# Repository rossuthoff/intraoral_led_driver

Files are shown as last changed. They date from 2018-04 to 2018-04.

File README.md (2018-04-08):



# intraoral led driver
Switching boost LED driver based on the Linear Technology [LT3478-1](http://www.analog.com/en/products/power-management/led-driver-ic/buck-boost-led-drivers/lt3478.html) chip. This LED driver is used for the oral cancer screening device described in [1]. 

## related repositories
This design requires the footprints found in the [kicad_footprints](https://github.com/rossuthoff/kicad_footprints) repository. Make sure the library and .mod files are added to your folder search locations. This board utilizes the [ytai/IOIO](https://github.com/ytai/ioio) microcontroller (MCU). Other microcontrollers that can send 3.3 V signals and control an I2C interface may be used. 

## general use
### power supply
LED driver is used in boost mode. The battery voltage must be less than the voltage drop across each individual LED string. Connector J5 supplies power to the MCU.

### led strings
Connect the LED strings to A+/A- and B+/B- connections. The LED string to be illuminated is controlled through a 3.3V signal to the sA or sB pins. The applied current is controlled through a Analog Devices [AD5247](http://www.analog.com/en/products/digital-to-analog-converters/digital-potentiometers/ad5247.html) digital potentiometer with an I2C interface.

# references
[1] Uthoff, R. D. et al. Development of a dual-modality, dual-view smartphone-based imaging system for oral cancer detection. in Proc. SPIE 10486, Design and Quality for Biomedical Technologies XI 10486, 104860V-10486–7 (SPIE, 2018).

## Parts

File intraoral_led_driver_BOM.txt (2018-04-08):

Reference	Locations	Value	Footprint	Notes	Manufacturer	PN	Distributor	Dist PN	Dist Link
C1	1	3.3uF	Capacitors_SMD:C_0603	25V	TDK Corporation	C1608X5R1E335K080AC	Digikey	445-14141-1-ND	https://www.digikey.com/product-detail/en/tdk-corporation/C1608X5R1E335K080AC/445-14141-1-ND/3955807
C2	1	4.7uF	Capacitors_SMD:C_1206	25V	TDK Corporation	C3216X5R1E475K160AA	Digikey	445-4047-2-ND	http://www.digikey.com/product-detail/en/tdk-corporation/C3216X5R1E475K160AA/445-4047-2-ND/1965635
C3	1	10uF	Capacitors_SMD:C_1812	25V	TDK Corporation	C4532X5R1E106M250KA	Digikey	445-3926-2-ND	http://www.digikey.com/product-detail/en/tdk-corporation/C4532X5R1E106M250KA/445-3926-2-ND/1923415
"C4, C6"	2	1uF	Capacitors_SMD:C_0603	25V	TDK Corporation	CGB3B1X5R1E105K055AC	Digikey	445-13224-2-ND	http://www.digikey.com/product-detail/en/tdk-corporation/CGB3B1X5R1E105K055AC/445-13224-2-ND/3950460
"C5, C7"	2	0.1uF	Capacitors_SMD:C_0603		TDK Corporation	C1608X8R1E104K080AA	Digikey	445-2500-2-ND	http://www.digikey.com/product-detail/en/tdk-corporation/C1608X8R1E104K080AA/445-2500-2-ND/927126
C8	1	10uF	Capacitors_Tantalum_SMD:CP_Tantalum_Case-A_EIA-3216-18_Reflow	10V	AVX Corporation	TPSA106K010R1800	Digikey	478-3317-1-ND	https://www.digikey.com/product-detail/en/avx-corporation/TPSA106K010R1800/478-3317-1-ND/930109
D1	1	D_Schottky_AAK	footprints:D_PowerDI-5		Diode Incorporated	PDS560-13	Digikey	PDS560DICT-ND	http://www.digikey.com/product-detail/en/diodes-incorporated/PDS560-13/PDS560DICT-ND/776779
D2	1	LED	footprints:LED_0603		Panasonic Electric Components	LNJ937W8CRA	Digikey	LNJ937W8CRATR-ND	http://www.digikey.com/product-detail/en/panasonic-electronic-components/LNJ937W8CRA/LNJ937W8CRACT-ND/2349027
"J1, J3"	2	CONN_01X04	Connectors_JST:JST_PH_S4B-PH-SM4-TB_04x2.00mm_Angled		JST Sales America	S4B-PH-SM4-TB(LF)(SN)	Digikey	455-1751-1-ND	https://www.digikey.com/product-detail/en/jst-sales-america-inc/S4B-PH-SM4-TB(LF)(SN)/455-1751-1-ND/926848
J2	1	CONN_01X03	Connectors_JST:JST_PH_S3B-PH-SM4-TB_03x2.00mm_Angled		JST Sales America	S3B-PH-SM4-TB(LF)(SN)	Digikey	455-1750-2-ND	https://www.digikey.com/product-detail/en/jst-sales-america-inc/S3B-PH-SM4-TB(LF)(SN)/455-1750-2-ND/926656
"J4, J5"	2	CONN_01X02	Connectors_JST:JST_PH_S2B-PH-SM4-TB_02x2.00mm_Angled		JST Sales America	S2B-PH-SM4-TB(LF)(SN)	Digikey	455-1749-2-ND	http://www.digikey.com/product-detail/en/jst-sales-america-inc/S2B-PH-SM4-TB(LF)(SN)/455-1749-2-ND/926655
L1	1	6.8uH	footprints:Sumida_L_CDRH105R		Sumida America Components	CDRH105RNP-6R8NC	Digikey	308-1927-2-ND	https://www.digikey.com/product-detail/en/sumida-america-components-inc/CDRH105RNP-6R8NC/308-1927-2-ND/3947171
"Q1, Q2"	2	Si2318DS-T1	TO_SOT_Packages_SMD:SOT-23		Vishay Siliconix	SI2318DS-T1-E3	Digikey	SI2318DS-T1-E3TR-ND	http://www.digikey.com/product-detail/en/vishay-siliconix/SI2318DS-T1-E3/SI2318DS-T1-E3DKR-ND/1764691
R1	1	100k	Resistors_SMD:R_0402	1%	Yageo	RC0402FR-07100KL	Digikey	311-100KLRTR-ND	http://www.digikey.com/product-detail/en/yageo/RC0402FR-07100KL/311-100KLRTR-ND/726526
R2	1	24k	Resistors_SMD:R_0402	1%	Yageo	RC0402FR-0724KL	Digikey	311-24KLRTR-ND	http://www.digikey.com/product-detail/en/yageo/RC0402FR-0724KL/311-24KLRTR-ND/2827581
R3	1	69.8k	Resistors_SMD:R_0402	1%	Yageo	RC0402FR-0769K8L	Digikey	YAG3216TR-ND	http://www.digikey.com/product-detail/en/yageo/RC0402FR-0769K8L/YAG3216TR-ND/5281076
"R4, R5, R7, R8"	4	10k	Resistors_SMD:R_0603	1%	Yageo	RC0603FR-0710KL	Digikey	311-10.0KHRTR-ND	https://www.digikey.com/product-detail/en/yageo/RC0603FR-0710KL/311-10.0KHRTR-ND/726880
R6	1	1k	Resistors_SMD:R_0603	1%	Yageo	RC0603FR-071KL	Digikey	311-1.00KHRTR-ND	https://www.digikey.com/product-detail/en/yageo/RC0603FR-071KL/311-1.00KHRTR-ND/726843
SW1	1	SW_SPST	footprints:C&K_SPST_switch_L101011MS02Q		C&K	L101011MS02Q	Digikey	CKC5106-ND	http://www.digikey.com/product-detail/en/c-k/L101011MS02Q/CKC5106-ND/484142
U1	1	LT3478-1	footprints:TSSOP-16-1EP_4.4x5mm_Pitch0.65mm		Linear Technologies	LT3478EFE-1#PBF	Digikey	LT3478EFE-1#PBF-ND	http://www.digikey.com/product-detail/en/linear-technology/LT3478EFE-1-PBF/LT3478EFE-1-PBF-ND/1619965
U3	1	AD5247	footprints:SC-70-6		Analog Devices	AD5247BKSZ10-RL7	Digikey	AD5247BKSZ10-RL7CT-ND	https://www.digikey.com/product-detail/en/analog-devices-inc/AD5247BKSZ10-RL7/AD5247BKSZ10-RL7CT-ND/1140637

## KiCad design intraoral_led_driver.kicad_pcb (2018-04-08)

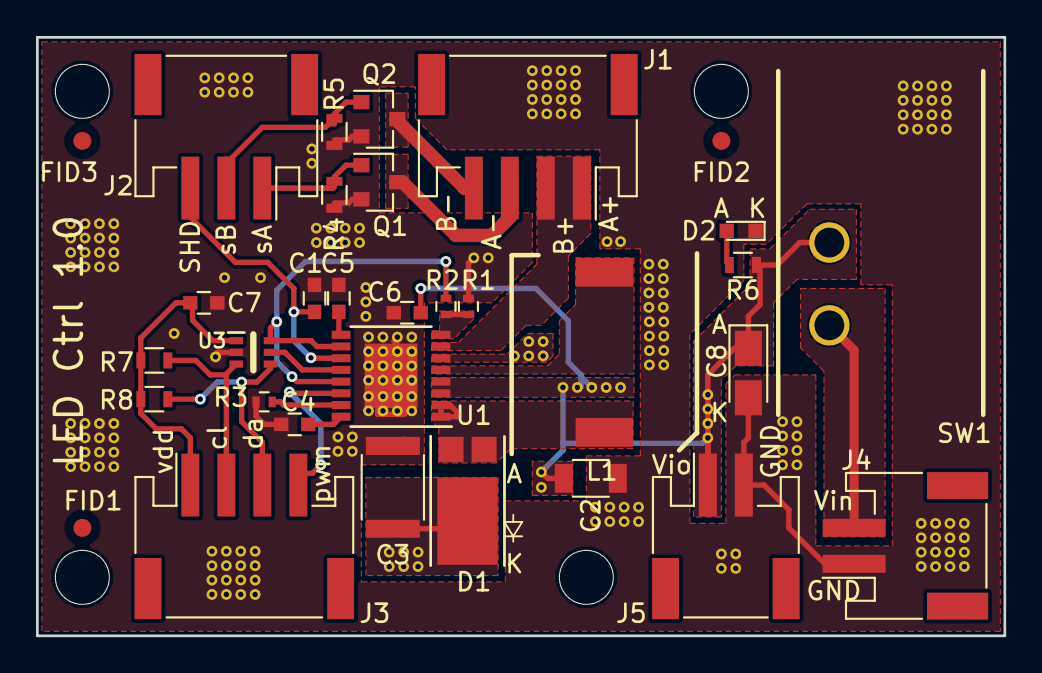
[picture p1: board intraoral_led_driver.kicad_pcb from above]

Board: 2 copper layers, 53.8 x 33.2 mm, 32 parts (0 on the bottom side), 23 nets.

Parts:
C1: 3.3uF; C_0603
C2: 4.7uF; C_1206
C3: 10uF; C_1812
C4, C6: 1uF; C_0603
C5, C7: 0.1uF; C_0603
C8: 10u; CP_Tantalum_Case-A_EIA-3216-18_Reflow
D1: D_Schottky_AAK; D_PowerDI-5
D2: LED; LED_0603
FID1, FID2, FID3: F_1mm; Fiducial_1mm_Dia_2mm_Outer_CopperTop
J1, J3: CONN_01X04; JST_PH_S4B-PH-SM4-TB_04x2.00mm_Angled
J2: CONN_01X03; JST_PH_S3B-PH-SM4-TB_03x2.00mm_Angled
J4, J5: CONN_01X02; JST_PH_S2B-PH-SM4-TB_02x2.00mm_Angled
L1: 6.8uH; Sumida_L_CDRH105R
Q1, Q2: Si2318DS-T1; SOT-23
R1: 100k; R_0402
R2: 24k; R_0402
R3: 69.8k; R_0402
R4, R5, R7, R8: 10k; R_0603
R6: 1k; R_0603
SW1: SW_SPST; C&K_SPST_switch_L101011MS02Q
U1: LT3478-1; TSSOP-16-1EP_4.4x5mm_Pitch0.65mm
U3: AD5247; SC-70-6

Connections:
/R_t: R3.2, U1.15
/SCL: J3.2, R7.1, U3.3
/SDA: J3.3, R8.1, U3.4
/SHDN: C1.1, J2.3, U1.11
/SS: C4.1, U1.16
/SW: D1.1, D1.2, L1.1, U1.1, U1.2
/Sig_V: J2.1, Q1.1, R4.1
/Sig_W: J2.2, Q2.1, R5.1
/V_DD: C7.1, J3.1, R7.2, R8.2, U3.1
/V_batt: J4.2, SW1.1
/V_c: C5.1, U1.9
/V_io: C2.1, C6.1, C8.1, J5.1, R6.2, SW1.2, U1.3, U1.4
/V_ref: R2.1, U1.10, U1.13, U3.6
/V_v+: J1.1, J1.2, U1.7
/V_v-: J1.3, Q1.3
/V_w-: J1.4, Q2.3
/ctrl1: U1.12, U3.5
/induc: L1.2, U1.5
/ovpset: R1.1, R2.2, U1.8
/pwm: J3.4, U1.14
/v_out: C3.1, D1.3, U1.6
GND: C1.2, C2.2, C3.2, C4.2, C5.2, C6.2, C7.2, C8.2, D2.1, J4.1, J5.2, Q1.2, Q2.2, R1.2, R3.1, R4.2, R5.2, U1.17, U3.2
unnamed: D2.2, R6.1

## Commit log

2018-04-08 update readme with citation. initial commit of design files
    [intraoral_led_driver-B.Cu.gbr, intraoral_led_driver-B.Mask.gbr, intraoral_led_driver-Edge.Cuts.gbr, intraoral_led_driver-F.Cu.gbr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]
2018-04-08 revert version to 1.0 for initial release. remove AOL logo
    [intraoral_led_driver.kicad_pcb]
2018-05-02 update for new connector
    [intraoral_led_driver-NPTH-drl_map.gbr, intraoral_led_driver.sch]
